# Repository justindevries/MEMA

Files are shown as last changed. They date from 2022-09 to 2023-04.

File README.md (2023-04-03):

# MEMA Build Files
An open-source, multiplexed potentiostat kit for at-home diagnostic testing, to be used in tandem with a custom microfluidic assay

This repository contains files for the hardware and firmware required to fabricate, assemble, and initialize the potentiostat.

For source code for complementary iOS app, please see [here](https://github.com/juliamstrauss/NFluidEX-iOS).

For source code for complementary Android app, please see [here](https://github.com/juliamstrauss/NFluidEX-Android).

MEMA is based on ABE-Stat, an open-source potentiostat designed by Jenkins et al. in 2019. Their open-source publication can be accessed [here](https://iopscience.iop.org/article/10.1149/2.0061909jes) for extensive documentation on the basis of its functionality.

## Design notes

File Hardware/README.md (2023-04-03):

# MEMA Hardware
Design and assembly files for manufacturing of the potentiostat's PCB and 3D-printed housing unit

For Arduino firmware files, please see [here](https://github.com/justindevries/NFluidEX/tree/main/Arduino).

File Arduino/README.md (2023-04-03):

# MEMA Arduino
Arduino firmware files for programming of the PCB microcontroller

For assembly files for PCB mannufacturing, please see [here](https://github.com/justindevries/NFluidEX/tree/main/Hardware).

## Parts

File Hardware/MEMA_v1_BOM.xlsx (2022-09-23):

 | Bill of Materials for pc board: "NFluidEX_v1" as of: 17/3/2022 1:44 PM
Ref | Item | Quantity | for 50 | w overage | Designator | Mfctr. Part Number | Description | Value | Package | Type | Manufacturer | Distributor | Dstbr. Part #
PSTAT1 | 1 | 1 | 50 | 150 | A1 | ESP-12F | ESP8266 WiFi Module |  |  |  | Adafruit Industries | Digikey | 1528-1438-ND
PSTAT2 | 2 | 1 | 50 | 150 | A2 | CYBLE-014008-00 | RX TXRX MODULE BT TRC ANT SMD |  |  | smt | Cypress Semiconductor Corp (http://digikey.com/Suppliers/us/Microchip-Technology.page?lang=en) | Digikey | 428-3600-1-ND
PSTAT3 | 3 | 17 | 850 | 950 | C1 - C17 | C0805C104K3RACTU | CAP CER 0.1UF 25V 10% X7R 0805 | 0.1 uF | 0805 | smt | Kemet (http://digikey.com/Suppliers/us/Kemet.page?lang=en) | Digikey | 399-1168-1-ND
PSTAT4 | 4 | 9 | 450 | 550 | C18 - C26 | C2012X5R1C106M085AC | CAP CER 10UF 16V 20% X5R 0805 | 10 uF | 0805 | smt | TDK Corporation (http://digikey.com/Suppliers/us/TDK.page?lang=en) | Digikey | 445-7645-2-ND
PSTAT5 | 5 | 4 | 200 | 300 | C27 - C30 | C0805C222K5RACTU | CAP CER 2200PF 50V X7R 0805 | 2200pF | 0806 | smt | KEMET (https://www.digikey.com/en/supplier-centers/k/kemet) | Digikey | 399-1151-1-ND
PSTAT6 | 6 | 3 | 150 | 250 | C31 - C33 | 08055C103KAT2A | CAP CER 10000PF 50V 10% X7R 0805 | 10000 pF | 0805 | smt | AVX Corporation (http://digikey.com/Suppliers/us/AVX.page?lang=en) | Digikey | 478-1383-1-ND
PSTAT7 | 7 | 3 | 150 | 250 | C34 - C36 | GRM219R61E475KA73D | CAP CER 4.7UF 25V X5R 0805 | 4.7 uF | 0805 | smt | Murata Electronics North America (https://www.digikey.com/en/supplier-centers/m/murata-electronics) | Digikey | 490-12753-1-ND
PSTAT8 | 8 | 2 | 100 | 200 | C37, C38 | CC0805JRX7R7BB224 | CAP CER 0.22UF 16V X7R 0805 | 0.22 uF | 0805 | smt | Yageo | Digikey | 311-4267-1-ND
PSTAT9 | 9 | 1 | 50 | 150 | C39 | 08055A100FAT2A | CAP CER 10PF 50V 1% NP0 0805 | 10 pF | 0805 | smt | AVX Corporation (http://digikey.com/Suppliers/us/AVX.page?lang=en) | Digikey | 478-10493-1-ND
PSTAT10 | 10 | 1 | 50 | 150 | C40 | EEF-CD0J470R | CAP ALUM POLY 47UF 20% 6.3V SMD | 47 uF | 7343 | smt | Panasonic Electronic Components (https://www.digikey.com/en/supplier-centers/p/panasonic) | Digikey | PCE3160CT-ND
PSTAT11 | 11 | 2 | 100 | 200 | D1, D2 | PMEG6010ER,115 | DIODE SCHOTTKY 60V 1A SOD123W |  | SOD123W | smt | Nexperia USA Inc. (https://www.digikey.com/en/supplier-centers/n/nexperia) | Digikey | 1727-5846-1-ND
PSTAT12 | 12 | 6 | 300 | 400 | FB1 - FB6 | 742792097 | FERRITE BEAD 1.5 KOHM 0805 1LN |  | 0805 | smt | Wurth Electronics Inc. (https://www.digikey.com/en/supplier-centers/w/wurth-electronics) | Digikey | 732-4649-1-ND
PSTAT13 | 13 | 1 | 50 | 60 | J1 | 1771127 | CONN TERM BLK 5POS 2.5MM SMD |  |  | smt | Phoenix Contact (https://www.digikey.com/en/supplier-centers/p/phoenix-contact) | Digikey | 277-2075-1-ND
PSTAT14 | 14 | 1 | 50 | 60 | J2 | 1771091 | CONN TERM BLK 2POS 2.5MM SMD |  |  | smt | Phoenix Contact (https://www.digikey.com/en/supplier-centers/p/phoenix-contact) | Digikey | 277-2072-1-ND
PSTAT15 | 15 | 1 | 50 | 60 | J3 | 629105136821 | CONN RCPT USB MICRO B R/A SMT |  |  | smt | Wurth Electronics Inc. (https://www.digikey.com/en/supplier-centers/w/wurth-electronics) | Digikey | 732-3155-1-ND
PSTAT16 | 16 | 1 | 50 | 60 | J4 | S2B-PH-SM4-TB(LF)(SN) | CONN HEADER PH SIDE 2POS 2MM SMD |  |  | smt | JST Sales America Inc. | Digikey | 455-1749-1-ND
PSTAT17 | 17 | 1 | 50 | 60 | J5 | 961106-6300-AR-PR | CONN HEADER VERT 6POS GOLD SMD |  |  | smt | 3M (https://www.digikey.com/en/supplier-centers/3/3m) | Digikey | 3M9488CT-ND
PSTAT18 | 18 | 1 | 50 | 60 | J8 | 1771101 | TERM BLK 3P TOP ENTRY 2.5MM SMD |  |  | smt | Phoenix Contact | Digikey | 277-2073-1-ND
PSTAT19 | 19 | 2 | 100 | 120 | LED1, LED2 | QBLP651-R | LED RED CLEAR 1206 SMD |  | 1206 | smt | QT Brightek (QTB) (https://www.digikey.com/en/supplier-centers/q/qt-brightek) | Digikey | 1516-1172-1-ND
PSTAT20 | 20 | 1 | 50 | 60 | LED3 | 150141M173100 | LED RGB CLEAR 1411 SMD |  |  | smt | Wurth Electronics Inc (http://www.digikey.com/Suppliers/us/Wurth-Electronics.page?lang=en) | DigiKey | 732-4998-1-ND
PSTAT21 | 21 | 5 | 250 | 275 | Q1 - Q5 | BSS138 | MOSFET N-CH 50V 220MA SOT-23 |  | SOT-23-3 | smt | Fairchild Semiconductor (http://digikey.com/Suppliers/us/Fairchild-Semiconductor.page?lang=en) | Digikey | BSS138CT-ND
PSTAT22 | 22 | 1 | 50 | 75 | Q6 | BSS84 | MOSFET P-CH 50V 130MA SOT-23 |  | SOT-23-3 | smt | Fairchild Semiconductor (http://digikey.com/Suppliers/us/Fairchild-Semiconductor.page?lang=en) | Digikey | BSS84CT-ND
PSTAT23 | 23 | 3 | 150 | 175 | Q7 - Q9 | DMP2160UW-7 | MOSFET P-CH 20V 1.5A SOT-323 |  |  |  | Diodes Incorporated (https://www.digikey.com/en/supplier-centers/d/diodes) | Digikey | DMP2160UWDICT-ND
PSTAT24 | 24 | 20 | 1000 | 1100 | R1 - R20 | ERJ-P06J103V | RES 10K OHM 1/2W 5% 0805 SMD | 10 k | 0805 | smt | Panasonic Electronic Components (http://digikey.com/Suppliers/us/Panasonic-Electronic-Components.page?lang=en) | Digikey | P10KADCT-ND
PSTAT25 | 25 | 6 | 300 | 400 | R21 - R26 | ERJ-P06J102V | RES SMD 1K OHM 5% 1/2W 0805 | 1 k | 0805 | smt | Panasonic Electronic Components (http://digikey.com/Suppliers/us/Panasonic-Electronic-Components.page?lang=en) | Digikey | P1.0KADCT-ND
PSTAT26 | 26 | 4 | 200 | 300 | R27 - R30 | ERJ-6GEYJ223V | RES SMD 22K OHM 5% 1/8W 0805 | 22k | 0805 | smt | Panasonic Electronic Components (http://digikey.com/Suppliers/us/Panasonic-Electronic-Components.page?lang=en) | Digikey | P22KACT-ND
PSTAT27 | 27 | 4 | 200 | 300 | R31 - R34 | ERA-6APB104V | RES SMD 100K OHM 0.1% 1/8W 0805 | 100k | 0805 | smt | Panasonic Electronic Components | Digikey | P100KAZCT-ND
PSTAT28 | 28 | 3 | 150 | 250 | R35 - R37 | ERJ-P06J332V | RES SMD 3.3K OHM 5% 1/2W 0805 | 3.3k | 0805 | smt | Panasonic Electronic Components (http://digikey.com/Suppliers/us/Panasonic-Electronic-Components.page?lang=en) | Digikey | P3.3KADCT-ND
PSTAT29 | 29 | 3 | 150 | 250 | R38 - R40 | ERA-6AEB103V | RES SMD 10K OHM 0.1% 1/8W 0805 | 10k | 0805 | smt | Panasonic Electronic Components | Digikey | P10KDACT-ND
PSTAT30 | 30 | 2 | 100 | 200 | R41, R42 | RG2012P-105-B-T5 | RES SMD 1M OHM 0.1% 1/8W 0805 | 1M | 0805 | smt | Panasonic Electronic Components | Digikey | RG20P1.0MBCT-ND
PSTAT31 | 31 | 2 | 100 | 200 | R43, R44 | ERJ-P6WJ101V | RES SMD 100 OHM 5% 1/2W 0805 | 100W | 0805 | smt | Panasonic Electronic Components (http://digikey.com/Suppliers/us/Panasonic-Electronic-Components.page?lang=en) | Digikey | P16942CT-ND
PSTAT32 | 32 | 1 | 50 | 150 | R45 | ERA-6AEB102V | RES SMD 1K OHM 0.1% 1/8W 0805 | 1k | 0805 | smt | Panasonic Electronic Components (https://www.digikey.com/en/supplier-centers/p/panasonic) | Digikey | P1.0KDACT-ND
PSTAT33 | 33 | 1 | 50 | 150 | R46 | ERJ-P06J202V | RES SMD 2K OHM 5% 1/2W 0805 | 2k | 0805 | smt | Panasonic Electronic Components (https://www.digikey.com/en/supplier-centers/p/panasonic) | Digikey | P2.0KADCT-ND
PSTAT34 | 34 | 1 | 50 | 150 | R47 | ERJ-P06J333V | RES SMD 33K OHM 5% 1/2W 0805 | 33k | 0805 | smt | Panasonic Electronic Components (https://www.digikey.com/en/supplier-centers/p/panasonic) | Digikey | P33KADCT-ND
PSTAT35 | 35 | 1 | 50 | 100 | R48 | ERJ-1TYJ2R0U | RES SMD 2 OHM 5% 1W 2512 | 2W | 2512 | smt | Panasonic Electronic Components (https://www.digikey.com/en/supplier-centers/p/panasonic) | Digikey | PT2.0XCT-ND
PSTAT36 | 36 | 3 | 150 | 160 | S1 - S3 | 1.14002.1110000 | SWITCH PUSH SPST-NO 0.1A 35V |  |  | smt | RAFI USA (https://www.digikey.com/en/supplier-centers/r/rafi) | Digikey | 1715-1675-1-ND
PSTAT37 | 37 | 1 | 50 | 60 | U1 | MCP73831T-2ACI/OT | IC CONTROLLR LI-ION 4.2V SOT23-5 |  | SOT23-5 | smt | Microchip Technology (https://www.digikey.com/en/supplier-centers/m/microchip-technology) | Digikey | MCP73831T-2ACI/OTCT-ND
PSTAT38 | 38 | 1 | 50 | 60 | U2 | AP7365-33EG-13 | IC REG LINEAR 3.3V 600MA SOT223 |  | SOT-2233L | smt | Diodes Incorporated (https://www.digikey.com/en/supplier-centers/d/diodes) | Digikey | AP7365-33EG-13DICT-ND
PSTAT39 | 39 | 1 | 50 | 60 | U3 | ISL60002BAH333Z-T7A | IC VREF SERIES 3.3V SOT23-3 | 3.3V | SOT-23-3 | smt | Intersil (https://www.digikey.com/en/supplier-centers/i/intersil) | Digikey | ISL60002BAH333Z-T7ACT-ND
PSTAT40 | 40 | 1 | 50 | 60 | U4 | TLE2426IDR | IC VREF GND REF ADJ 8SOIC |  | 8SOIC | smt | Texas Instruments | Digikey | 296-1345-1-ND
PSTAT41 | 41 | 2 | 100 | 110 | U5, U6 | MM74HC595MTCX | IC SHIFT REGISTER 8-BIT 16-TSSOP |  | 16-TSSOP | smt | Fairchild/ON Semiconductor (https://www.digikey.com/en/supplier-centers/f/fairchild) | Digikey | MM74HC595MTCXCT-ND
PSTAT42 | 42 | 2 | 100 | 110 | U7, U8 | 74LVC1G53DC,125 | IC MUX/DEMUX 2X1 8VSSOP |  | 8VSSOP | smt | Nexperia USA Inc. (https://www.digikey.com/en/supplier-centers/n/nexperia) | Digikey | 1727-3492-1-ND
PSTAT43 | 43 | 2 | 100 | 110 | U9, U10 | ADG779BKSZ-REEL7 | IC SWITCH SPDT SC70-6 |  | SC-70-6 | smt | Analog Devices Inc. (https://www.digikey.com/en/supplier-centers/a/analog-devices) | Digikey | ADG779BKSZ-REEL7CT-ND
PSTAT44 | 44 | 1 | 50 | 60 | U11 | AD5933YRSZ-REEL7 | NETWORK ANALYZER 12B 1MSP 16SSOP |  | 16SSOP | smt | Analog Devices Inc. | Digikey | AD5933YRSZ-REEL7CT-ND
PSTAT45 | 45 | 1 | 50 | 60 | U12 | ADS1220IPWR | IC ADC 24-BIT 2KSPS 16-TSSOP |  | 16-TSSOP | smt | Analog Devices Inc. | Digikey | 296-39851-1-ND
PSTAT46 | 46 | 1 | 50 | 60 | U13 | AD5061BRJZ-2REEL7 | IC DAC 16BIT SPI/SRL SOT23-8 |  | SOT23-8 | smt | Analog Devices Inc. | Digikey | AD5061BRJZ-2REEL7CT-ND
PSTAT47 | 47 | 1 | 50 | 60 | U14 | ADG715BRUZ | IC SWITCH OCTAL SPST 24TSSOP |  | 24TSSOP | smt | Analog Devices Inc. | Digikey | ADG715BRUZ-ND
PSTAT48 | 48 | 1 | 50 | 60 | U15 | SN74LVC2G86DCUR | IC GATE XOR 2CH 2-INP US8 | XOR | US8 | smt | Texas Instruments (http://digikey.com/Suppliers/us/Texas-Instruments.page?lang=en) | Digikey | 296-13275-1-ND
PSTAT49 | 49 | 1 | 50 | 60 | U16 | ADG704BRMZ | IC MULTIPLEXER 4X1 10USOIC |  | 10USOIC | smt | Analog Devices Inc. | Digikey | ADG704BRMZ-ND
PSTAT50 | 50 | 1 | 50 | 60 | U17 | LMP7721MA/NOPB | IC AMP PREC 3FA BIAS CURR 8SOIC |  | 8SOIC | smt | Texas Instruments (http://digikey.com/Suppliers/us/Texas-Instruments.page?lang=en) | Digikey | LMP7721MA/NOPB-ND
PSTAT51 | 51 | 3 | 150 | 160 | U18 - U20 | LMP7702MM/NOPB | IC OPAMP GP 2.5MHZ RRO 8VSSOP |  | 8-MSOP | smt | Texas Instruments | Digikey | LMP7702MM/NOPBCT-ND
PSTAT52 | 52 | 2 | 100 | 110 | U21, U22 | LMP7715MF/NOPB | IC OPAMP GP 17MHZ RRO SOT23-5 |  | SOT23-5 | smt | Texas Instruments | Digikey | LMP7715MF/NOPBCT-ND
PSTAT53 | 53 | 1 | 50 | 60 | X1 | DSC6083CI2A-250K000 | OSC MEMS 250.0000KHZ CMOS SMD | 250kHz | 4-SMD | smt | Microchip Technology | Digikey | DSC6083CI2A-250K000-ND
 |  | 142

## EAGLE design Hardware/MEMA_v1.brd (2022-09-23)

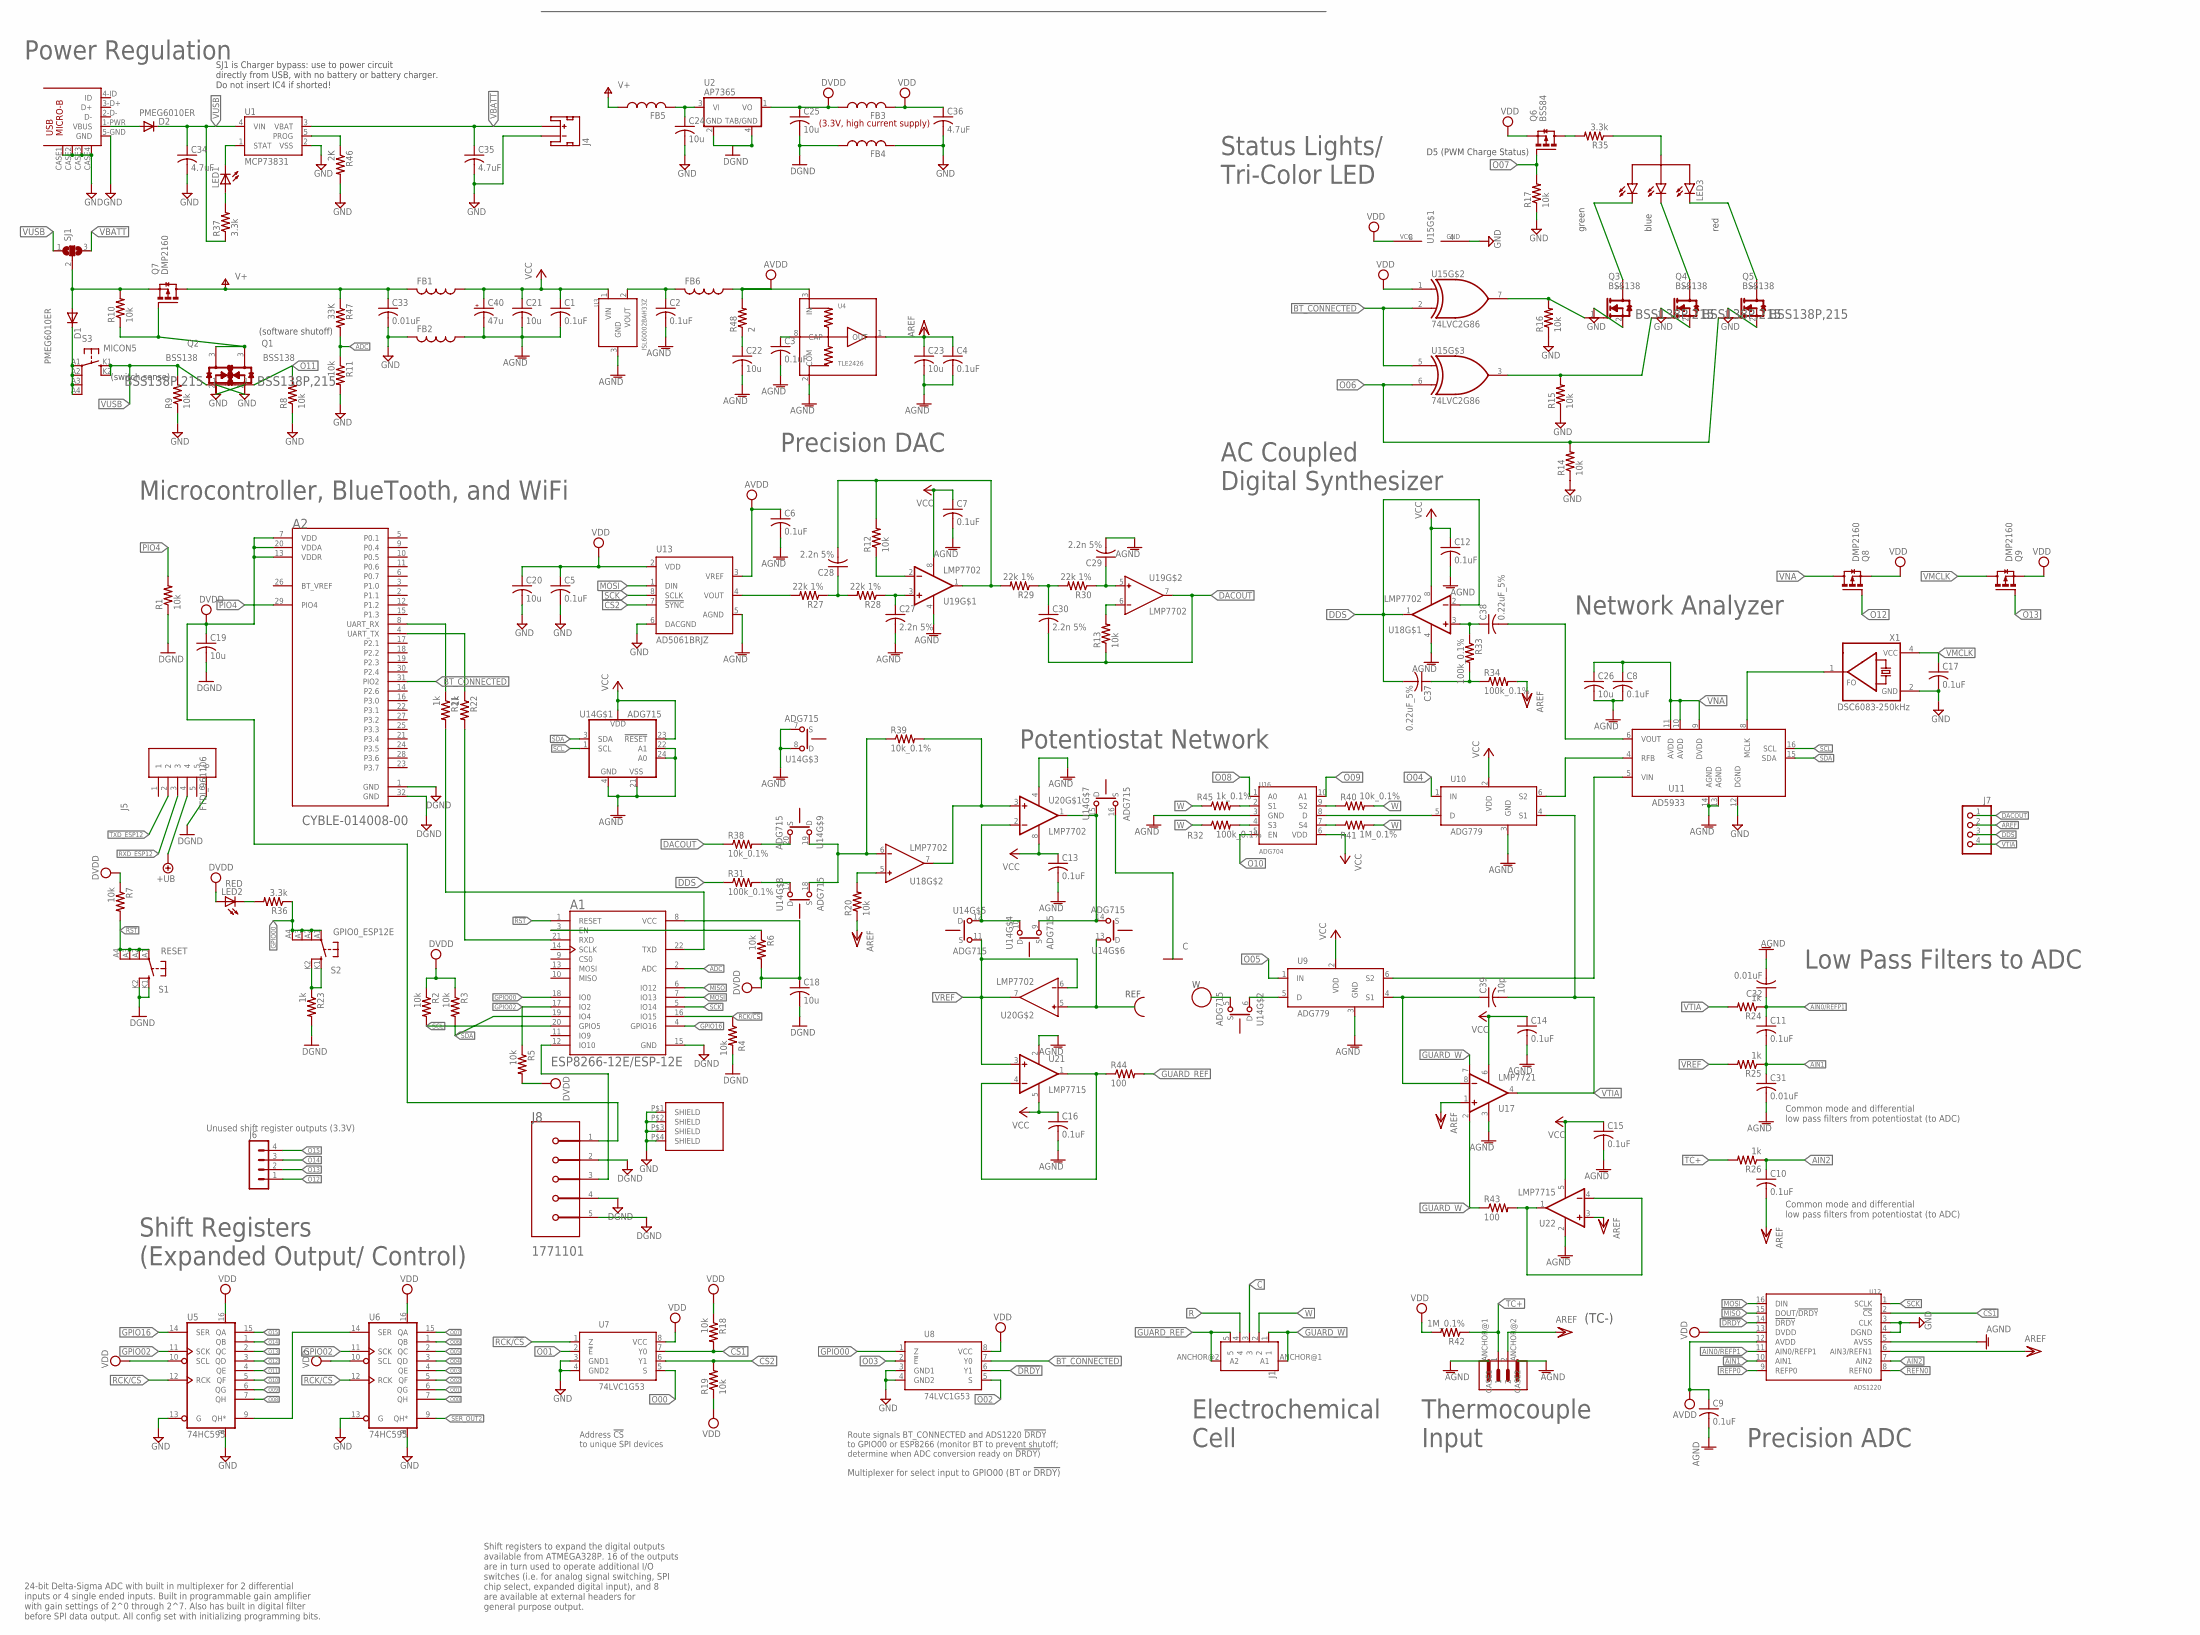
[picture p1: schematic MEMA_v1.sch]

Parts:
A1: ESP8266-12E/ESP-12E; XCVR_ESP8266-12E/ESP-12E
A2: CYPRESS_SEMICONDUCTOR_CYBLE-014008-00CYPRESS_SEMI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; CYPRESS_SEMICONDUCTOR_CYBLE-014008-00_0
C1, C2, C3, C4, C5, C6, C7, C8, C9, C10, C11, C12, C13, C14, C15, C16, C17: 0.1uF; C0805
C18, C19, C20, C21, C22, C23, C24, C25, C26: 10u; C0805
C27, C28, C29, C30: 2.2n 5%; C0805
C31, C32, C33: 0.01uF; C0805
C34, C35, C36: 4.7uF; C0805
C37, C38: 0.22uF_5%; C0805
C39: 10p; C0805
C40: 47u; D/7343-31W
D1, D2: PMEG6010ER; DIODE_SOD123
FB1, FB2, FB3, FB4, FB5, FB6: FERRITE_BEAD_5A_0805; R0805
J1: 5-PIN-VERTICAL-PHOENIX_2.5MM-SMD; 5-PIN-VERT_PHOENIX_SMD
J2: 1A_JENKINS_2013_2PIN_SMD_PHOENIX_CONTACTVERTICAL; 2-PIN-VERT_PHOENIX_SMD
J3: USB-MICRO-B; USB_MICRO_B_WURTH_629105136821
J4: JST_2MM_MALE; JST-2-SMD
J5: FTDI_961106; TSM-106-XX-XXX-SV
J6: MA04-1
J7: PINHD-1X4; 1X04
J8: PHOENIX_CONTACT_1771101PHOENIX_CONTACT_1771101_0_0; PHOENIX_CONTACT_1771101_0
LED1: LEDCHIPLED_1206; CHIPLED_1206
LED2: RED; LED-1206
LED3: LED_RBG_COM_ANODE; LED_RGB_WURTH_150141M173100
Q1, Q2, Q3, Q4, Q5: BSS138; NEXPERIA_BSS138P_215_0
Q6: BSS84; SOT-23-3
Q7, Q8, Q9: DMP2160; SOT-23-3
R1, R2, R3, R4, R5, R6, R7, R8, R9, R10, R11, R12, R13, R14, R15, R16, R17, R18, R19, R20: 10k; R0805
R21, R22, R23, R24, R25, R26: 1k; R0805
R27, R28, R29, R30: 22k 1%; R0805
R31, R32, R33, R34: 100k_0.1%; R0805
R35, R36, R37: 3.3k; R0805
R38, R39, R40: 10k_0.1%; R0805
R41, R42: 1M_0.1%; R0805
R43, R44: 100; R0805
R45: 1k_0.1%; R0805
R46: 2K; R0805
R47: 33K; R0805
R48: 2; R2512
S1: RESET; RAFI-MICON5_SWITCH
S2: GPIO0_ESP12E; RAFI-MICON5_SWITCH
S3: MICON5; RAFI-MICON5_SWITCH
SH1: SMARTDART_SHIELD; SMARTDART-SHIELD
SJ1: SJ2W; SJ_2
U1: MCP73831; SOT23-5
U2: AP7365; SOT-223
U3: ISL60002BAH33Z; SOT-23-3
U4: TLE2426; SOIC-8
U5, U6: 74HC595; TSSOP16
U7, U8: 74LVC1G53; VSSOP8
U9, U10: ADG779; SC70-6
U11: AD5933; SSOP-16
U12: ADS1220; TSSOP16
U13: AD5061BRJZ; SOT-23-8
U14: ADG715; TSSOP24
U15: 74LVC2G86; US-8
U16: ADG704; MSOP10
U17: LMP7721; SOIC-8
U18, U19: LMP7702; UMAX8
U20: LMP7702; MSOP8
U21, U22: LMP7715; SOT23-5
X1: DSC6083-250kHz; DSC60XX_OSCILLATOR_3.2X2.5MM

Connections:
!CS1: R18.2, U7.7 (Y0), U12.2 (!CS)
!CS2: R19.2, U7.6 (Y1), U13.7 (!SYNC)
!DRDY: U8.6 (Y1), U12.14 (!DRDY)
!RST: A1.1 (RESET), R7.2, S1.A1, S1.A2 (P1), S1.A3 (P2), S1.A4 (P3)
+UB: J5.4
AD5933_VIN: U9.6 (S2), U11.5 (VIN)
ADC: A1.2 (ADC), R11.1, R47.2
AGND: C1.2, C2.2, C3.2, C4.2, C6.2, C7.2, C8.2, C9.2, C12.2, C13.2, C14.2, C15.2, C16.2, C21.2, C22.2, C23.2, C26.2, C27.2, C29.2, C31.2, C32.2, C40.-, FB2.1, J2.ANCHOR@1 (CASE1), J2.ANCHOR@2 (CASE2), U3.3 (GND), U4.2 (COM), U9.3 (GND), U10.3 (GND), U11.13 (AGND), U11.14 (AGND), U12.5 (AVSS), U13.5 (AGND), U14.4 (GND), U14.7 (S), U14.8 (D), U14.21 (VSS), U14.22 (A1), U14.24 (A0), U16.3 (GND), U17.3 (V-), U18.4 (V-), U19.4 (V-), U20.4 (V-), U21.2 (V-), U22.2 (V-)
AIN0/REFP1: C11.1, C32.1, R24.1, U12.11 (AIN0/REFP1)
AIN1: C11.2, C31.1, R25.1, U12.10 (AIN1)
AIN2: C10.1, R26.1, U12.7 (AIN2)
AREF: C4.1, C10.2, C23.1, J2.2, J7.2, R20.1, R34.2, U4.1 (OUT), U12.6 (AIN3/REFN1), U17.1 (+IN), U22.3 (+IN)
AVDD: C6.1, C9.1, FB6.1, R48.2, U4.3 (IN), U12.12 (AVDD), U13.3 (VREF)
BT_CONNECTED: A2.31 (PIO2), U8.7 (Y0), U15.2 (I1), U15.5 (I0)
BT_VREF: A2.26 (BT_VREF)
C: J1.3, U14.16 (S)
DACOUT: C30.2, J7.1, R13.1, R38.1, U19.7 (OUT)
DDS: C37.2, J7.3, R31.1, U18.1 (OUT), U18.2 (-IN)
DGND: A1.15 (GND), A2.1 (GND), A2.32 (GND), C18.2, C19.2, C25.2, FB4.1, J5.6, J8.2, J8.4 (MNT_1), J8.5 (MNT_2), R1.1, R4.2, R23.2, S1.K1 (S), S1.K2 (S1), U2.2 (GND), U2.4 (GND1)
DVDD: A1.8 (VCC), A2.7 (VDD), A2.13 (VDDR), A2.20 (VDDA), C18.1, C19.1, C25.1, FB3.1, J8.1, LED2.A, R2.1, R3.1, R5.2, R6.2, R7.1, U2.1 (VO)
GND: C5.2, C17.2, C20.2, C24.2, C33.2, C34.2, C35.2, C36.2, FB2.2, FB4.2, J3.5-GND (GND), J3.CASE1 (CASE), J3.CASE2 (CASE), J3.CASE3 (CASE), J3.CASE4 (CASE), J4.1 (-), Q1.2 (S), Q2.2 (S), Q3.2 (S), Q4.2 (S), Q5.2 (S), R8.1, R9.1, R11.2, R14.1, R15.1, R16.1, R17.1, R46.2, SH1.P$1, SH1.P$2, SH1.P$3, SH1.P$4, U1.2 (VSS), U5.8 (GND), U5.13 (G), U6.8 (GND), U6.13 (G), U7.3 (GND1), U7.4 (GND2), U8.3 (GND1), U8.4 (GND2), U11.12 (DGND), U12.3 (CLK), U12.4 (DGND), U13.6 (DACGND), U15.4 (GND), X1.2 (GND)
GPIO00: A1.18 (IO0), R36.1, S2.A1, S2.A2 (P1), S2.A3 (P2), S2.A4 (P3), U8.1 (Z)
GPIO02: A1.17 (IO2), R5.1, U5.11 (SCK), U6.11 (SCK)
GPIO10: A1.12 (IO10), J8.3
GPIO16: A1.4 (GPIO16), U5.14 (SER)
GUARD_REF: J1.5, J1.ANCHOR@2 (A2), R44.2
GUARD_W: J1.1, J1.ANCHOR@1 (A1), R43.1, U17.2 (GUARD), U17.7 (GUARD)
MISO: A1.6 (IO12), U12.15 (DOUT/!DRDY)
MOSI: A1.7 (IO13), U12.16 (DIN), U13.1 (DIN)
unnamed: A2.8 (UART_RX), R21.1
unnamed: U14.10 (D), U14.12 (D), U20.2 (-IN)
unnamed: D2.A, J3.1-PWR (VBUS)
unnamed: A2.4 (UART_TX), R22.1
unnamed: Q3.1 (G), R16.2, U15.7 (O)
unnamed: U9.5 (D), U14.6 (D)
unnamed: R46.1, U1.5 (PROG)
unnamed: U5.9 (QH*), U6.14 (SER)
unnamed: C27.1, R28.1, U19.3 (+IN)
unnamed: LED1.C, U1.1 (STAT)
unnamed: R27.2, U13.4 (VOUT)
unnamed: LED1.A, R37.2
unnamed: C22.1, R48.1
unnamed: R31.2, U14.17 (D)
unnamed: C28.1, R27.1, R28.2
unnamed: R23.1, S2.K1 (S), S2.K2 (S1)
unnamed: Q4.1 (G), R15.2, U15.3 (O)
unnamed: D1.C, S3.A1, S3.A2 (P1), S3.A3 (P2), S3.A4 (P3)
unnamed: C3.1, U4.8 (CAP)
unnamed: C28.2, R12.2, R29.2, U19.1 (OUT)
unnamed: C30.1, R29.1, R30.2
unnamed: C29.1, R30.1, U19.5 (IN+)
unnamed: R12.1, U19.2 (-IN)
unnamed: U14.9 (S), U14.14 (S), U14.15 (D), U20.1 (OUT)
unnamed: R13.2, U19.6 (IN-)
unnamed: LED2.C, R36.2
unnamed: C2.1, FB6.2, U3.2 (VOUT)
unnamed: C39.1, U9.4 (S1), U17.8 (-IN)
unnamed: R39.1, U14.18 (S), U14.19 (D), U18.6 (IN-)
unnamed: R39.2, U18.7 (OUT), U20.3 (+IN)
unnamed: U10.6 (S2), U11.4 (RFB)
unnamed: R41.1, U16.7 (S4)
unnamed: R44.1, U21.1 (OUT), U21.4 (-IN)
unnamed: R40.1, U16.9 (S2)
unnamed: Q1.3 (D), Q2.3 (D), Q7.1 (G), R10.1
unnamed: U10.5 (D), U16.8 (D)
unnamed: R45.2, U16.2 (S1)
unnamed: R32.2, U16.4 (S3)
unnamed: LED3.G, Q3.3 (D)
unnamed: R43.2, U22.1 (OUT), U22.4 (-IN)
unnamed: LED3.B, Q4.3 (D)
unnamed: LED3.R, Q5.3 (D)
unnamed: Q6.3 (D), R35.2
unnamed: LED3.A, R35.1
unnamed: R38.2, U14.20 (S)
unnamed: C24.1, FB5.2, U2.3 (VI)
unnamed: A1.3 (EN), R6.1
unnamed: U11.8 (MCLK), X1.1 (FO)
unnamed: D1.A, Q7.2 (S), R10.2, SJ1.2
unnamed: R20.2, U18.5 (IN+)
unnamed: C37.1, R33.2, R34.1
unnamed: C38.1, R33.1, U18.3 (+IN)
unnamed: C38.2, U11.6 (VOUT)
O00: U6.7 (QH), U7.5 (S)
O01: U6.6 (QG), U7.2 (!E)
O02: U6.5 (QF), U8.5 (S)
O03: U6.4 (QE), U8.2 (!E)
O04: U6.3 (QD), U10.1 (IN)
O05: U6.2 (QC), U9.1 (IN)
O06: Q5.1 (G), R14.2, U6.1 (QB), U15.6 (I1)
O07: Q6.1 (G), R17.2, U6.15 (QA)
O08: U5.7 (QH), U16.1 (A0)
O09: U5.6 (QG), U16.10 (A1)
O10: U5.5 (QF), U16.5 (EN)
O11: Q1.1 (G), R8.2, U5.4 (QE)
O12: J6.1, Q8.1 (G), U5.3 (QD)
O13: J6.2, Q9.1 (G), U5.2 (QC)
O14: J6.3, U5.1 (QB)
O15: J6.4, U5.15 (QA)
PIO4: A2.29 (PIO4), R1.2
R: J1.4, U14.13 (D), U20.5 (IN+)
RCK/!CS: A1.16 (IO15), R4.1, U5.12 (RCK), U6.12 (RCK), U7.1 (Z)
REFN0: U12.8 (REFN0)
REFP0: U12.9 (REFP0)
RXD_ESP12: A1.21 (RXD), J5.3, R22.2
SCK: A1.5 (IO14), U12.1 (SCLK), U13.8 (SCLK)
SCL: A1.20 (GPIO5), R2.2, U11.16 (SCL), U14.1 (SCL)
SDA: A1.19 (IO4), R3.2, U11.15 (SDA), U14.3 (SDA)
SER_OUT2: U6.9 (QH*)
TC+: J2.1, R26.2, R42.1
TXD_ESP12: A1.22 (TXD), J5.2, R21.2
V+: C33.1, FB1.2, FB5.1, Q7.3 (D), R47.1
VBATT: C35.1, J4.2 (+), SJ1.3, U1.3 (VBAT)
VCC: C1.1, C7.1, C12.1, C13.1, C14.1, C15.1, C16.1, C21.1, C40.+, FB1.1, U3.1 (VIN), U9.2 (VDD), U10.2 (VDD), U14.2 (VDD), U14.23 (!RESET), U16.6 (VDD), U17.6 (V+), U18.8 (V+), U19.8 (V+), U20.8 (V+), U21.5 (V+), U22.5 (V+)
VDD: C5.1, C20.1, C36.1, FB3.2, Q6.2 (S), Q8.2 (S), Q9.2 (S), R18.1, R19.1, R42.2, U5.10 (SCL), U5.16 (VCC), U6.10 (SCL), U6.16 (VCC), U7.8 (VCC), U8.8 (VCC), U12.13 (DVDD), U13.2 (VDD), U15.1 (I0), U15.8 (VCC)
VMCLK: C17.1, Q9.3 (D), X1.4 (VCC)
VNA: C8.1, C26.1, Q8.3 (D), U11.9 (DVDD), U11.10 (AVDD), U11.11 (AVDD)
VREF: R25.2, U14.11 (S), U20.6 (IN-), U20.7 (OUT), U21.3 (+IN)
VTIA: C39.2, J7.4, R24.2, U10.4 (S1), U17.4 (OUT)
VUSB: C34.1, D2.C, Q2.1 (G), R9.2, R37.1, S3.K1 (S), S3.K2 (S1), SJ1.1, U1.4 (VIN)
W: J1.2, R32.1, R40.2, R41.2, R45.1, U14.5 (S)

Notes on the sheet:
(3.3V, high current supply)
Route signals BT_CONNECTED and ADS1220 !DRDY to GPIO00 or ESP8266 (monitor BT to prevent shutoff; determine when ADC conversion ready on !DRDY)
Shift registers to expand the digital outputs available from ATMEGA328P. 16 of the outputs are in turn used to operate additional I/O switches (i.e. for analog signal switching, SPI chip select, expanded digital input), and 8 are available at external headers for general purpose output.
Multiplexer for select input to GPIO00 (BT or !DRDY)
Power Regulation
Microcontroller, BlueTooth, and WiFi
Precision ADC
Shift Registers (Expanded Output/ Control)
24-bit Delta-Sigma ADC with built in multiplexer for 2 differential inputs or 4 single ended inputs. Built in programmable gain amplifier with gain settings of 2^0 through 2^7. Also has built in digital filter before SPI data output. All config set with initializing programming bits.
Common mode and differential low pass filters from potentiostat (to ADC)
Address !CS to unique SPI devices
(switch sense)
(software shutoff)
Precision DAC
Network Analyzer
Potentiostat Network
Low Pass Filters to ADC
Thermocouple Input
Electrochemical Cell
D5 (PWM Charge Status)
green
blue
red
Status Lights/ Tri-Color LED
(TC-)
Unused shift register outputs (3.3V)
REF
SJ1 is Charger bypass: use to power circuit directly from USB, with no battery or battery charger. Do not insert IC4 if shorted!
AC Coupled Digital Synthesizer

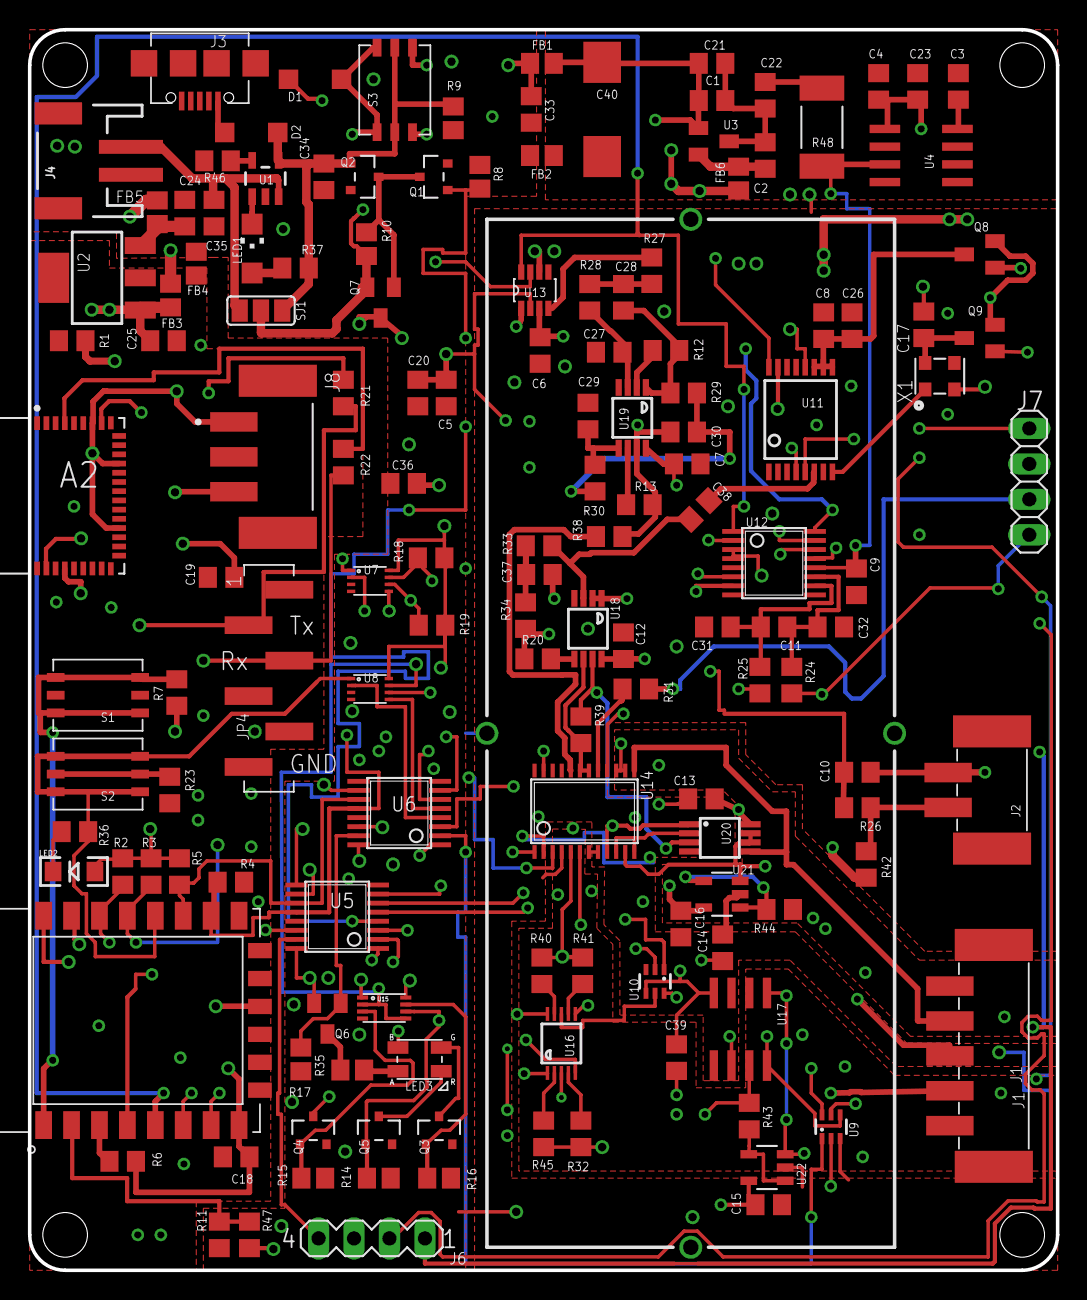
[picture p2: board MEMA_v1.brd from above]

Board: 4 copper layers, 73.7 x 88.9 mm, 146 parts (0 on the bottom side), 115 nets.

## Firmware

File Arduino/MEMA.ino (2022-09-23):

/*
  February 14, 2017 (Started as NC1194_Potentiostat.ino)

  Updated March 23, 2017- largely to address hardware design changes on new design iteration NC1194 Potentiostat V3. These include use of i2c octal switch ADG715 for 
  potentiostat signal switching (A0 and A1 on ADG715 pulled to ground, so i2c address is 0x48). Network analyzer AD5933 address is 0x0D. Other changes are use of 
  low dropout 3.3V regulator AP7365 for wireless devices (high side switching transistor of TPS 62172was not able to deliver required current from single cell Lithium battery),
  corrected i2c pinout for ESP8266 (GPIO5 for SCL, GPIO4 for SDA), and reconfigured potentiostat network (error made in earlier designs).

  Updated dates up to about April 24, 2017- include code to read and communicate temperature, and impedance register values from AD5933 for given frequency, as well as
  current and voltage applied through transimpedance amplifier...

  Updated (to version 04_Exp) on April 30, 2017, for testing various functionality necessary for development of more fully developed Android GUI.

  Changed name to ABE-Stat_1_0_03 (previous versions in summer 2017) on August 20, 2017, mostly to run different basic measurement features of NC1194 Potentiostat. Version 1_0_03 is the
  first to include specific analytical methods (i.e. starting with cyclic voltammetry and electrochemical impedance spectroscopy); ABE-Stat_1_0_04 first version to implement EIS; also polishing
  up CV...

  ABE-Stat 1_0_5 started September 8, 2017- building on fully functional ABE-Stat1_0_04 which has calibration routines including for battery, EIS functions using AD5933 (from 5 kHz to 100 kHz),
  CV functions up to 0.2 scan rate. Adding EIS functionality from 0.1Hz to about 100 Hz using signals generated entirely from DAC5061, and DFT of TIA samples from ADS1220 (in this case running 
  in turbo mode at highest data rate 2000 sps...

  ABE-Stat 1_0_06 started September 14, 2017; admittance vs frequency calibrations change with different AD5933 settings (i.e. PGAx5GainSetting, excitationCode, and TIAGainCode;
  so update calibration routines to calibrate admittance magnitude (scaled by load resistor from calibration
  Version 06_worked on through September 26 2017 to include open circuit configuration and open circuit voltage measurement (i.e. pH electrode); upgraded this version through
  September 26 to include calibration for every setting of AD5933, and all basic interfaces with Android ABE-Stat app through Cyclic Voltammetry and Electrochemical
  Impedance spectroscopy, including for low frequencies using ADC (ADS1220) for customized single frequency DFT...

  ABE-Stat_1_0_07 started September 27, 2017; simple check for TIA saturation not always effective (at saturation amplifier inputs violate ideality(?) and the observed TIA output voltage 
  is not always close to positive analog rail value (i.e. in some instances is lower than 1 V)- so updated resistance measurement, current measurements, and EIS measurements
  to confirm linearity of a result at a different setting before accepting a value... Also, added methods to conduct Differential Pulse Voltammetry.
  Also included a firmware number to report back to Android... Also tried to check all calculated values for divide by 0 to prevent "nan" or "inf" being written to Android when it expects
  a parsable number string...

  ABE-Stat_1_0_08 October 26; add code to shut off power after 1 minute idle with no bluetooth connection.
  ABE-Stat_1_0_09 November 3, 2017; blink LED a few times and turn off if battery is discharged; corrected EEPROM_Int_Write so that 16 bit value gets written to two 8 bit blocks (previously LSB overwrites MSB)

  ABE-Stat_1_0_10 December 15, 2017, turn off WiFi at startup, and keep off to suppress noise; also increase update rates for CV to try to smooth applied potential

  ABE-Stat_1_01_00 started January 19, 2018, update functions to use external clock 250kHz clock with AD5933 for lower frequency EIS; update requires updated board design ABE-Stat_1.0.01
  (previous versions worked with NC-1194_Potentiostat). Need to add additional EEPROM and calibration assignments to calibrate device operating over new frequencies and clock,
  and ABE-Stat_DigitalConfigurations (i.e. !O12 controls power enable to AD5933 and external clock- leave off for other voltammetric applications to limit noise).
  Also update DigitalConfigurations to use ADG715 S02 to make biasing amplifier a voltage follower for open circuit configuration (don't allow unpredictable leakage from drifting
  output). (used for preliminary testing of EIS with MCLK external clock, and also some troubleshooting to improve LED modulation for indicating charge state)

  ABE-Stat_1_01_02 started February 21, 2018; start developing calibration of EIS with external MCLK, and defining best frequency ranges for each setting (?).

  ABE-Stat_1_01_03 started May 9, 2018; to work with hardware version ABE-Stat 1_0_02, (separate power controller on O13 for AD5933 external clock); device also attempts to correct
  750 Hz harmonic distortion observed in version 01

  ABE-Stat_1_01_07, starting July 6, 2018 building on last stable version ABE-Stat_1_01_03 (versions 1_01_04 to 1_01_05 are transitional codes that either won't compile, or resulted in 
  issues of such as analog switches not behaving predictably / reproducibly(?)), so here we salvage some of the improvements in approach for reliable EIS from version 1_01_06
  Generally, when using AD5933 for the first measurement an optimization routine is called to test every gain and PGA setting at the given excitation signal (bias and amplitude)
  to identify the one that results in the best quality data (saturation will result in an overprediction of impedance, so setting is chosen with the highest digitized admittance value

  ABE-Stat_1_01_08, starting July 6, 2018 building on last stable version ABE-Stat_1_01_03 (versions 1_01_04 to 1_01_05 are transitional codes that either won't compile, or resulted in 
  issues of such as analog switches not behaving predictably / reproducibly(?)), version 1.01.07 successfully updated testImpedance function to with a separate startAD5933Synthesizer
  and readAD5933Data functions, and averages 10 successive readings... Here we try to also incorporate the function to automitically identify the optimal test settings...

  ABE-Stat_1_01_09, starting July 12, 2018 quickly hard code observed bias on AD5933 working vs system analog reference (so we can correct for to apply correct bias for EIS)
   Also hard code correction for frequency, and send back EIS results at every available setting to reconstruct spectra...

  ABE-Stat_1_01_10, starting August 10, 2018 add new functionality for generic logging function (i.e. log potential in current for configurable electrode network / applied potential),
    i.e. for chronoamperometry

  ABE-Stat_1_01_11, starting August 25, 2018 force all analytical / multimeter functions to send code ('j') inside iterative loops to prevent Android device from timing out and
    disconnecting, and several other debugs to prevent system timeout which especially might cause ABE-Stat to lock up without ability to reset / self-shutoff

  ABE-Stat_1_01_12, starting August 26, 2018 upgrades timing functions for CV (replace "delay(1)" with yield(); delay(1) was especially problematic given that DAC increment period
    is 1 ms...; also used micros() for timing instead of millis() (a bad choice for 1 ms interval time for updating DAC value); also corrected issue with electrode configuration commands
    not being reliable- evidently i2c commands are not read by ADG715 octal analog switch if AD5933 (on shared i2c bus) is not powered- so always ensure that AD5933 is powered
    during instructions to change electrode configuration.

  ABE-Stat_1_01_13, starting August 27, 2018 Polish up a few last items, i.e. allow uniform user defined (log scale) intervals for EIS, and calibrate frequency AD5933 internal clock
     and correspondingly ensure that frequency values reported for EIS are accurate (each device will operate with slightly different frequencies).

  ABE-Stat_1_01_14, starting September 19, 2018 Recover battery charge reporting functionality not working correctly in recent versions; return electrode configuration back to open
    open circuit potential after completion of every analytical method (prevents undesired application of corrosive potentials on networks / electrodes when not in use)...
    (Note, actually poor battery monitoring performance is related to low (out of spec) range of ESP8266 ADC on many devices (full scale should go to 1.0 V, but evidently the
    scale / reference is significantly smaller on many ESP8266 chips...

  ABE-Stat_1_01_15, starting October 1, 2018; chooses the correct feedback resistance to prevent TIA saturation while "equilibrating" at desired potential on CV and DPV
    (saturation can diminish "equilibrating" potential and redox currents- biasing measurements as system corrects saturation problem (this is an issue for systems where
    currents would exceed 10 uA under the desired potential, using highest gain setting. Symptom of problem is big tail on starting redox current...

  ABE-Stat_1_01_16, starting October 28, 2018; checks current and increases gain if observed current is sub-optimal (i.e. predicted TIA voltage from increased gain does not 
     saturate amplifier) (ultimately algorithm uses previous impedance estimate to predict settings for new measurement to prevent saturation- approach works best starting at
     low frequencies with high impedance, and using small increments in EIS frequency measurement so large changes in impedance don't occur between successive measurements...

  ABE-Stat_1_01_17, starting November 19, 2018; change thresholds for predicting saturation (i.e. some fixed resistor EIS increases in "observed" impedance when measuring with network
    analyzer (i.e. above 60 Hz impedance reported for ~3300 Ohm resistor is ~5100 Ohm). Also try to fix problem where second EIS scan gets hung up in open circuit configuration.
    Predicted TIA voltage threshold changed from 1.2 V to 1.0 V...
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

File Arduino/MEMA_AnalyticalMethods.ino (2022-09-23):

/*
 * Creator: Daniel M. Jenkins
 * Date: August 20, 2017
 * Description: First functions for parsing instructions to conduct an electrochemical / analytical method and reporting data back to ABE-Stat.apk...
 * 
 */
 
/*
 * Parse command for selected analytical method...
 * Note that electrode configuration is not set here- make sure it is set in the main "loop" function before getting sent here!
 */
 void startAnalyticalMethod() {
    redLED(true);
    illuminateLED();
    boolean ex = false;
    while (!ex) {
      while (!Serial.available());
      command = Serial.read();
      switch(command) {
        case 'a':
          AnodicStrippingVoltammetry();
          ex = true; // always exit analytical method routine when selected method is complete...
          break;
        case 'c':
          CyclicVoltammetry();
          ex = true; // always exit analytical method routine when selected method is complete...
          break;
        case 'd':
          DifferentialPulseVoltammetry();
          ex = true; // always exit analytical method routine when selected method is complete...
          break;
        case 'e':
          ElectrochemicalImpedanceSpectroscopy();
          ex = true; // always exit analytical method routine when selected method is complete...
          break;
        case 'l':
          staticLogging();
          ex = true;
          break;
        case 'x':// exit calibration routine
          ex = true;
          break;
        default:
          ex = true;
          break;
      }
    }
    electrodeConfig = OPEN_CIRCUIT_CONFIG;  // make sure that at end of every routine we go back to open circuit configuration (don't apply undesired potential to network- may denature enzymes!
    resetElectrodeConfig();
    redLED(false); // turn off red LED- process complete...
}

void AnodicStrippingVoltammetry() {
      
}

/*
 * Static logging merely sends current and potential data back every time Android requests it, using the best resolution measurements.
 * Make sure android doesn't request data more than 10x per second (0.1s sampling period) or it will outrun the ADC data rate resulting
 * in major delays later!
 */
void staticLogging() {
      TIA_LMP7721();  // set TIA to return to LMP7721 and ADS1220 ADC...
      DAC_AD5061_Connect(true); // connect DAC from AD5061 to network...
      AD5933_Connect(false);
      setTIAGain(0x03); // initially start at most sensitive gain (will dial down if offscale later)
      double E = Serial.parseFloat();  // start potential (in V)
      //setElectrodeConfig(); // reads one character; '2' or '3' for corresponding # electrode configuration, any other or '0' for open circuit configuration (this is already set for chosen analysis before getting sent to analytical method routines)
      DAC_AD5061_SetCalibratedVoltage(E);  // first set the potential at the starting value...
      if (electrodeConfig == OPEN_CIRCUIT_CONFIG) {
          DAC_AD5061_Connect(false);  // if open circuit configuration, just disconnect DAC from network
          DAC_AD5061_SetCalibratedVoltage(0.00);  // and set it to 0V output (make sure we're not putting any bias on control amplifier that might bleed to network)..
      }
      Configure_ADS1220();  // basic configuration for ADC (normal mode, slowest data rate 20 SPS, 50 and 60Hz recursive filters active, for best quality resolution / performance)
      double currentGarbage = cellCurrent();  // just invoke cellCurrent() function to one more time to find TIAGain setting for measuring current before actually recording data.
      
      boolean endOfAnalysis = equilibrationPeriod();  // request the duration of equilibration period; returns "true" if user exits analysis during equilibration...
      
      /*ADS1220_ReportTemperature();  // don't send these data unsolicitedly- they will foul up the indexing scheme for data / Time on Android
      ReportVoltammetryValues(0.0);*/// report observed values of cell potential and current- not a differential measurement so just send 0.0 for "preStepCurrent" (this value is subtracted from the measured current value)
      batteryReport();
      
      while (!endOfAnalysis) {
          if (Serial.available()) { // listen for instructions to exit, or send new voltammetry values...
                  char instruction = Serial.read();
                  switch (instruction) {
                    case 'v':
                        ADS1220_ReportTemperature();
                        ReportVoltammetryValues(0.0);
                        batteryReport();
                        break;
                    case 'x':
                        endOfAnalysis = true; // instruction received to exit analysis...
                        break;
                    default:
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

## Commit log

2022-09-23 PCB Layout Files
    [NFluidEX_v1.brd, NFluidEX_v1.sch, NFluidEX_v1_BOM.xlsx, NFluidEX_v1_centroid.csv]
2022-09-23 CAM Outputs
    [copper_bottom_l4.gbr, copper_inner_l2.gbr, copper_inner_l3.gbr, copper_top_l1.gbr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]
2022-09-23 Housing Unit CAD Files

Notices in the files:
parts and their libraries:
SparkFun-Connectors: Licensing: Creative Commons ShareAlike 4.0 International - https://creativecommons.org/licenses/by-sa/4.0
